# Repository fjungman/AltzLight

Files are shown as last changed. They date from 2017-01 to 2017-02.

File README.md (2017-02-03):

# AltzLight
Flashing a string of LEDs at 40Hz to combat Alzheimer's 

Runs on Adafruit Feather using Arduino 1.8.1 compiler
Add all sound files in the "cuts" directory to the root of a micro SD card.  Do not change the file names.
Schematic Word document shows how to interconnect the two boards.
The .mp3 files are processed by the Adafruit "Music Maker" shield (P1788).  
The SD card is placed in the Music Maker shield, and NOT in the Feather (if it even has an SD card slot).
I used 30V/60A TO-220 N-Chaneel power MOSFETs (like Adafruit P355), with one FET per color of the LED strip.  
So, a total of 4 MOSFETs (R, G, B and White).
Power is applied to the strips (12VDC) on teh black wire, then feeds through the LEDs and into the FETs (low-side switching).
The gates are driven by the Feather outputs 10, 11, 12 & 13.  These are setup for 40Hz/40% duty cycle.
The sources are all tied together and directly to ground.
Low impedance paths should be used for the 12v stuff, so thicker wires and short runs.
I ran three 6' strings in parallel, so my total 12V current could hit 28A!  That is divided into four FETs, so each FET doesn't see
more than 7A, so they run very cool.
I added a PowerTail II Switch to kill the 12V, but this is not totally needed.  
If I forgot to unplug it and the FETs turned on a little, they could get very hot and cause a fire, so I kill the 12V at the end of the code, using the PowerTail and GPIO 18 (marked as "A4" on the Feather)
The light starts up on initial boot and says Hi.  It then waits for the user to press a button.
The button is connected to GPIO 19 (A5).
Each press of the button adds 15 minutes of run time, and is debounced.
The unit limits total run time to three hours.
Each press will speak the time remaining.
Every five minutes, the time remaining will be announced.
At the end, the last minute will be counted down in 10 second intervals.
When the last minute is over, a goodbye message is played and then the lights are turned off.
The lights turn off by taking the lights from 100% duty cycle to 0% duty cycle over about 40 seconds.
Before this, a warning that they are turning off and a request to turn on the room lights is played.
Once the duty cycle hits zero, the outputs are turned off and the PowerTail is switched off, then an endless loop is entered.

The sound files in "Cuts" are all .mp3 files that are called by filename in the program.  Numbers are called by converting the current number needed (such as "35" in 35 minutes) to a string, appending ".mp3" to it, and running it through the call to the Music Maker play file routine.  Note:  The Music Maker rountine only uses 8.3 naming convention, and I don't check for that, so if you call a file with a longer filename than 8 characters, it won't play and won't throw an error.

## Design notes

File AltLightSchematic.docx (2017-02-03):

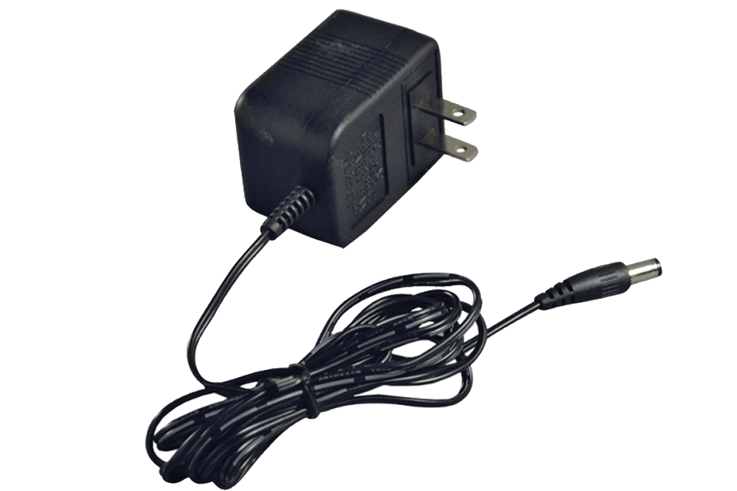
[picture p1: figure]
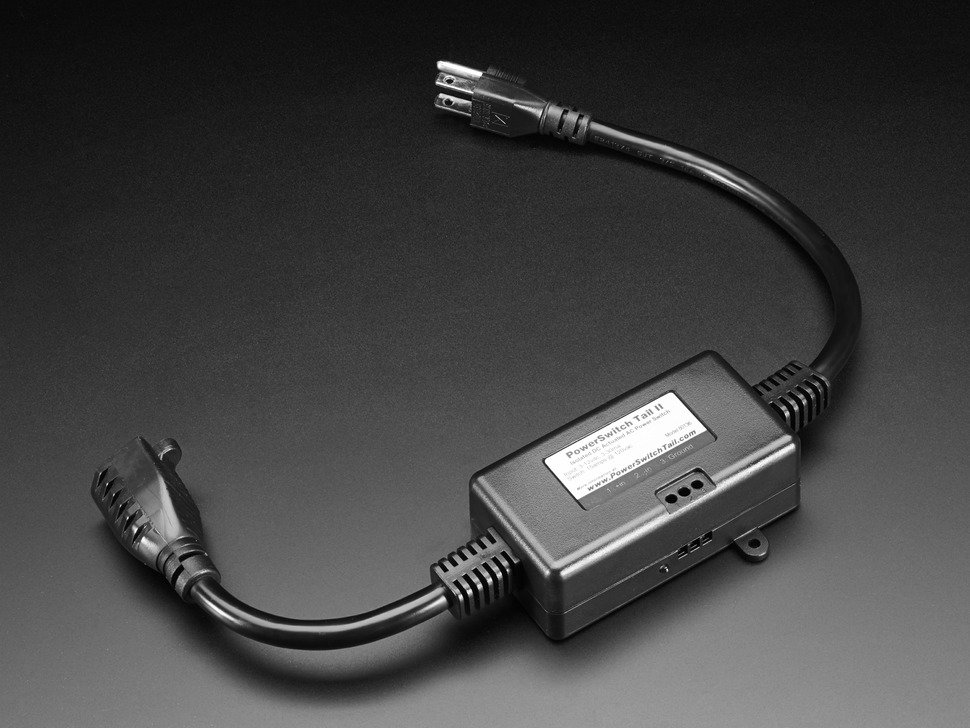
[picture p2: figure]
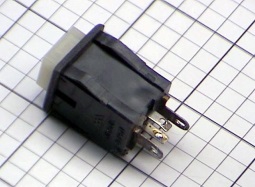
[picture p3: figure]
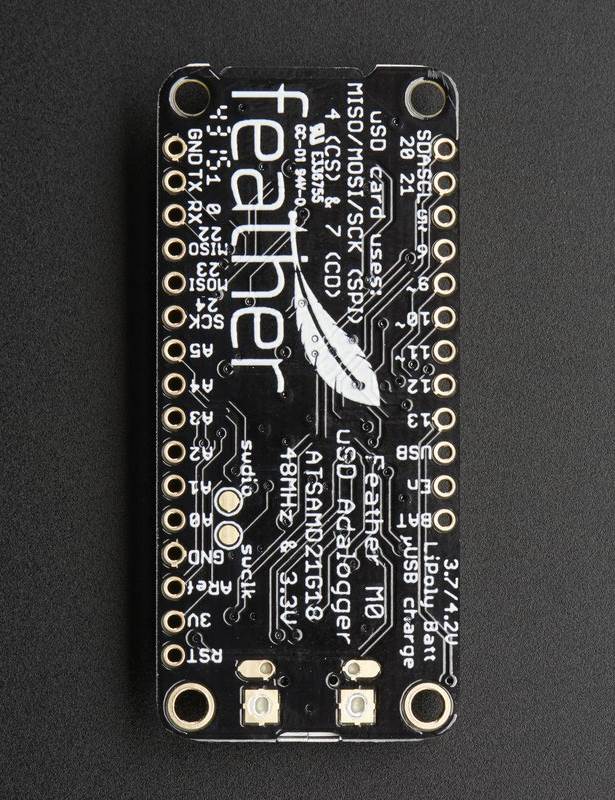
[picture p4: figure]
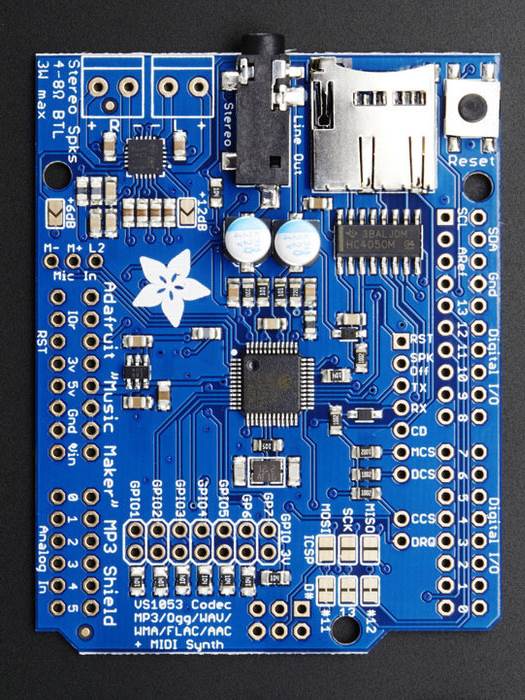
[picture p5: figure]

+12VDC to Black Wire

Cut off the connector

To Speakers

From Feather GIPOs

To FET Gates

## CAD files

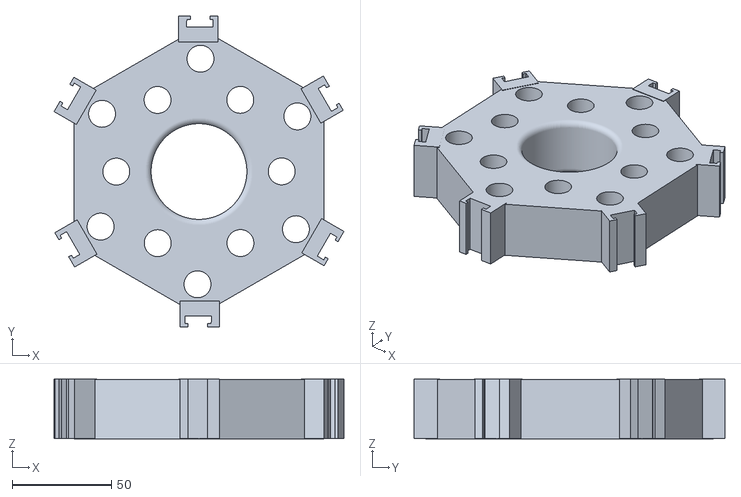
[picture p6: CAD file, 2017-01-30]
MidHolder.stl
146.2 x 156.8 x 30.2

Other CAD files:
Holder with button mount.stl

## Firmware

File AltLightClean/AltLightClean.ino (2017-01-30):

//###############################################################################
// Declarations Section
//###############################################################################

const byte interruptPin = 19; // Use A5 for Input Button wire
volatile bool ButtonPress = 0;  // Setup bit for tracking the press
int minutes = 0;
bool finished = 1;
unsigned long lastSecond = 0;
int seconds = 0;
int fives = 0;
bool complete = 0;
bool started = 0;
bool justSpoke = 0;
char *Filename = new char[13];
char *NumSecs = new char[3];
char *MPString = ".mp3";
char *MinChar = new char[7];
char *SecChar = new char[7];

// Specifically for use with the Adafruit Feather, the pins are pre-set here!

// include SPI, MP3 and SD libraries
#include <SPI.h>
#include <SD.h>
#include <string.h>
#include <Adafruit_VS1053.h>

// These are the pins used
#define VS1053_RESET   -1     // VS1053 reset pin (not used!)

// Feather M0 or 32u4  <----- This is used for Altz Light!
#if defined(__AVR__) || defined(ARDUINO_SAMD_FEATHER_M0)
  #define VS1053_CS       6     // VS1053 chip select pin (output)
  #define VS1053_DCS      0     // VS1053 Data/command select pin (output)
  #define CARDCS          5     // Card chip select pin
  // DREQ should be an Int pin *if possible* (not possible on 32u4)
  #define VS1053_DREQ     9     // VS1053 Data request, ideally an Interrupt pin
#endif


Adafruit_VS1053_FilePlayer musicPlayer = 
  Adafruit_VS1053_FilePlayer(VS1053_RESET, VS1053_CS, VS1053_DCS, VS1053_DREQ, CARDCS);

//###############################################################################
// Setup - main  -> This runs once
//###############################################################################
void setup()
{
  //  ****  FOR DEBUG ONLY ---- Setup Serial Terminal  -------  *******
  // Serial.begin(115200);
  // Wait for serial port to be opened, remove this line for 'standalone' operation
  // while (!Serial) { delay(1); }

  // Serial.println("\n\nAdafruit VS1053 Feather Test");
  //  ****  END DEBUG ONLY ---- Setup Serial Terminal  -------  *******
  
  
  // First, configure PWMs on pins 10 to 13 for 40Hz at 40% duty cycle
  
  REG_GCLK_GENDIV = GCLK_GENDIV_DIV(3) |          // Divide the 48MHz clock source by divisor 3: 48MHz/3=16MHz
                    GCLK_GENDIV_ID(4);            // Select Generic Clock (GCLK) 4
  while (GCLK->STATUS.bit.SYNCBUSY);              // Wait for synchronization

  REG_GCLK_GENCTRL = GCLK_GENCTRL_IDC |           // Set the duty cycle to 50/50 HIGH/LOW
                     GCLK_GENCTRL_GENEN |         // Enable GCLK4
                     GCLK_GENCTRL_SRC_DFLL48M |   // Set the 48MHz clock source
                     GCLK_GENCTRL_ID(4);          // Select GCLK4
  while (GCLK->STATUS.bit.SYNCBUSY);              // Wait for synchronization now 6
  
  // Enable the port multiplexer for the digital pin D11(PA16), D13(PA17). D10(PA18), D12(PA19)
  PORT->Group[g_APinDescription[11].ulPort].PINCFG[g_APinDescription[11].ulPin].bit.PMUXEN = 1;
  PORT->Group[g_APinDescription[13].ulPort].PINCFG[g_APinDescription[13].ulPin].bit.PMUXEN = 1;
  PORT->Group[g_APinDescription[10].ulPort].PINCFG[g_APinDescription[10].ulPin].bit.PMUXEN = 1;
  PORT->Group[g_APinDescription[12].ulPort].PINCFG[g_APinDescription[12].ulPin].bit.PMUXEN = 1;

  // Connect the TCC0 timer to digital output D13 = PA17 = ODD - port pins are paired odd PMUO and even PMUXE
  // F & E specify the timers: TCC0, TCC1 and TCC2
  PORT->Group[g_APinDescription[11].ulPort].PMUX[g_APinDescription[11].ulPin >> 1].reg = PORT_PMUX_PMUXO_E | PORT_PMUX_PMUXE_E;
  PORT->Group[g_APinDescription[10].ulPort].PMUX[g_APinDescription[10].ulPin >> 1].reg = PORT_PMUX_PMUXO_F | PORT_PMUX_PMUXE_F;

  // Feed GCLK4 to TCC2 (and TC3)
  REG_GCLK_CLKCTRL = GCLK_CLKCTRL_CLKEN |         // Enable GCLK4 to TCC2 (and TC3)
                     GCLK_CLKCTRL_GEN_GCLK4 |     // Select GCLK4
                     GCLK_CLKCTRL_ID_TCC2_TC3;    // Feed GCLK4 to TCC2 (and TC3)
  while (GCLK->STATUS.bit.SYNCBUSY);              // Wait for synchronization

  // Feed GCLK4 to TCC0 and TCC1
  REG_GCLK_CLKCTRL = GCLK_CLKCTRL_CLKEN |         // Enable GCLK4 to TCC0 and TCC1
                     GCLK_CLKCTRL_GEN_GCLK4 |     // Select GCLK4
                     GCLK_CLKCTRL_ID_TCC0_TCC1;   // Feed GCLK4 to TCC0 and TCC1
  while (GCLK->STATUS.bit.SYNCBUSY);              // Wait for synchronization

  // Dual slope PWM operation: timers countinuously count up to PER register value then down 0
  REG_TCC2_WAVE |= TCC_WAVE_POL(0xF) |            // Reverse the output polarity on all TCC2 outputs
                   TCC_WAVE_WAVEGEN_DSBOTH;       // Setup dual slope PWM on TCC2
  while (TCC2->SYNCBUSY.bit.WAVE);               // Wait for synchronization

  // Dual slope PWM operation: timers countinuously count up to PER register value then down 0
  REG_TCC0_WAVE |= TCC_WAVE_POL(0xF) |            // Reverse the output polarity on all TCC0 outputs
                   TCC_WAVE_WAVEGEN_DSBOTH;       // Setup dual slope PWM on TCC0
  while (TCC0->SYNCBUSY.bit.WAVE);               // Wait for synchronization

  // Each timer counts up to a maximum or TOP value set by the PER register,
  // this determines the frequency of the PWM operation:
  REG_TCC2_PER = 50100; // Set the frequency of the PWM on TCC2 to 40Hz
  while (TCC2->SYNCBUSY.bit.PER);                // Wait for synchronization

  // Each timer counts up to a maximum or TOP value set by the PER register,
  // this determines the frequency of the PWM operation:
  REG_TCC0_PER = 50100; // Set the frequency of the PWM on TCC0 to 40Hz
  while (TCC0->SYNCBUSY.bit.PER);                // Wait for synchronization

  // Set the PWM signal to output 20ms and 20ms
  REG_TCC2_CC0 = 20000;                              // TCC2 CC0 - on D11
  REG_TCC2_CC1 = 20000;                      // TCC2 CC1 - on D13
  while (TCC2->SYNCBUSY.bit.CC1);                   // Wait for synchronization

  // Set the PWM signal to output 20ms and 20ms
  REG_TCC0_CC2 = 20000;                            // TCC0 CC0 - on D10
  REG_TCC0_CC3 = 20000;                           // TCC0 CC1 - on D12
  while (TCC0->SYNCBUSY.bit.CC3);                 // Wait for synchronization

  // Divide the 12MHz signal by 4 giving 3MHz (333.33ns) TCC2 timer tick and enable the outputs
  REG_TCC2_CTRLA |= TCC_CTRLA_PRESCALER_DIV4 |    // Divide GCLK4 by 4
                    TCC_CTRLA_ENABLE;             // Enable the TCC2 output
  while (TCC2->SYNCBUSY.bit.ENABLE);              // Wait for synchronization

  // Divide the 12MHz signal by 4 giving 3MHz (333.33ns) TCC0 timer tick and enable the outputs
  REG_TCC0_CTRLA |= TCC_CTRLA_PRESCALER_DIV4 |    // Divide GCLK4 by 4
                    TCC_CTRLA_ENABLE;             // Enable the TCC0 output
  while (TCC0->SYNCBUSY.bit.ENABLE);              // Wait for synchronization

// Setup IO pins for GPIO tasks

  pinMode(interruptPin, INPUT_PULLUP);  // Setup button input pin
  attachInterrupt(digitalPinToInterrupt(interruptPin), buttonIn, FALLING);  // Trigger on falling edge
  pinMode(8, OUTPUT);
  pinMode(18, OUTPUT);  // Line to control power switch for LED power supply
  minutes = 0;
  seconds = 0;
  finished = 1;

  digitalWrite(8, LOW);
  digitalWrite(18, LOW);  // Make sure power is off to LEDs
  
// Setup Music Player
  musicPlayer.begin();
  SD.begin(CARDCS);
  musicPlayer.setVolume(10,10);
  musicPlayer.useInterrupt(VS1053_FILEPLAYER_PIN_INT);


  musicPlayer.playFullFile("HiDad.mp3");  // Say Hi Daddy!

// Wait here for first button press
  while(!ButtonPress) {
    delay(1);
  }
// Setup millisecond counter
lastSecond = millis();
// Turn on power to LED Strip Power Supply

  digitalWrite(18, HIGH);  // Turn on LEDs
}
 
//###############################################################################
// Loop - main
//###############################################################################
 
// This loop detects the button press, adds 15 minutes to the run time, runs 
// and then shuts down.  It speaks the run time as the button is pressed.
// During running, it will announce a message every five minutes
// When shutting down, it will leave the lights on and warn that lights will go out
// in one minute, then run a timer and fade the lights at the end while saying
// "goodbye"
// Time is kept in only minutes and seconds.
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

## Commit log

2017-01-30 More initial uploading
    [Holder with button mount.stl, MidHolder.stl]
2017-01-30 Datasheet on LED strip I used
